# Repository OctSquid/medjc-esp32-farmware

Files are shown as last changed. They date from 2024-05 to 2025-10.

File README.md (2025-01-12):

# MEDJC09-HUB

## 概要

乾式筋電センサ`MEDJC-09`を最大 3 台まで制御できるハブデバイス</br>
センサの電圧読み取りは`MCP3208`を使用する．

## ハードウェア構成

[回路図](./docs/pcb.md)

- マイコン : ESP32
- ADC : `MCP3208`
- 筋電センサ : `MEDJC-09` 最大 3 台

### ADC チャネル対応

| チャネル番号 |     説明      |
| :----------: | :-----------: |
|     `0`      | MED`0`のME値  |
|     `1`      | MED`0`のSME値 |
|     `2`      | MED`1`のME値  |
|     `3`      | MED`1`のSME値 |
|     `4`      | MED`2`のME値  |
|     `5`      | MED`2`のSME値 |
|     `6`      |  ベース電圧   |

## コマンドフォーマット

ホストから UART で特定のコマンドを定められたバイナリフォーマットで送信する．</br>
バイナリの送信受信には[PacketSerial](https://github.com/bakercp/PacketSerial/tree/master)が使用される．</br>
送受信されるパケットは`COBS`エンコードされる．以下のフォーマットはデコード後のバイナリフォーマットである．

### 送信コマンド(HOST -> ESP32)

```bash
<コマンド> <ID> <パラメータ(オプション)>
[CMD] [ID] [PRM]
```

- `コマンド` : コマンド一覧のコマンドを送信する．コマンド一覧を参照．
- `ID` : コマンド送受信を対応させるための識別子. 16bit符号なし整数.
- `パラメータ` : コマンドによって送信するパラメータのサイズは異なる．

### 応答コマンド(ESP32 -> HOST)

コマンドが正常に処理された場合，ACK 応答を経た後，応答コマンドを返す．</br>

```bash
<応答コマンド> <ID> <パラメータ(オプション)>
[CMD] [ID] [PRM]
```

- `応答コマンド` : コマンド一覧の応答コマンドを返す．
- `ID` : コマンド送受信を対応させるための識別子. 16bit符号なし整数.
- `パラメータ` : コマンドによって返すパラメータのサイズは異なる．

> [!NOTE]
> すべてのコマンドはCOBSエンコードされて送受信されます。

### ERR 応答(ESP32 -> HOST)

コマンドが正常に処理されなかった場合，エラーコマンドを返す．</br>
特定のコマンドに対応するエラーコードがある．

```bash
# 0xFE <ERRコード> 0xFD
[SER] [ERRCode] [EER]
```

- `SERTX` : エラー応答の開始を示す．エラー応答の開始には必ず SERTX`0xFE`を返す．
- `ERRコード` : エラーコードを返す．ERR コード一覧を参照．
- `EERTX` : エラー応答の終了を示す．エラー応答の終了には必ず EERTX`0xFD`を返す．

#### ERR コード一覧(共通)

| ERR コード |               エラー内容               |
| :--------: | :------------------------------------: |
|   `0x01`   |            コマンド構文不正            |
|   `0x11`   |   コマンド無効(対応するコマンドなし)   |
|   `0x21`   | パラメータ無効(対応するパラメータなし) |

### コマンド一覧

- ファームウェアバージョンの取得
- ベース電圧の取得
- センサの接続状態の確認
- センサの ME 読み取り
- センサの SME 読み取り

| コマンド | コマンド名 |          コマンド説明          |
| :------: | :--------: | :----------------------------: |
|  `0x00`  |   `PING`   |       デバイスの生存確認       |
|  `0x01`  |  `GETVER`  | ファームウェアバージョンの取得 |
|  `0x02`  |  `GETBV`   |        ベース電圧の取得        |
|  `0x20`  |  `GETCON`  |     センサの接続状態の確認     |
|  `0x30`  |  `GETME`   |      センサの ME 読み取り      |
|  `0x31`  |  `GETSME`  |     センサの SME 読み取り      |
|  `0x40`  |  `STAPRM`  | ポーリングレポートモードの開始 |
|  `0x41`  |  `ENDPRM`  | ポーリングレポートモードの終了 |
|  `0x42`  |  `SETPRR`  | ポーリングレポートレートの設定 |
|  `0x43`  |  `GETPRR`  | ポーリングレポートレートの取得 |
|  `0x4F`  |  `GETPR`   |    ポーリングレポートの取得    |

#### デバイスの生存確認

デバイスの生存確認を行う．

- 送信コマンド

```bash
0x00 [ID]
```

- 応答コマンド

```bash
0x00 [ID]
```

#### ファームウェアバージョンの取得

デバイスのファームウェアバージョンを取得する．

- 送信コマンド

```bash
0x01 [ID]
```

- 応答コマンド

```bash
0x01 [ID] [MJV] [MIV] [PTV]
# EX) 0x01 0x0000 0x01 0x00 0x00 -> v1.0.0
```

| パラメータ | サイズ  |        説明        |
| :--------: | :-----: | :----------------: |
|   `MJV`    | `1byte` | メジャーバージョン |
|   `MIV`    | `1byte` | マイナーバージョン |
|   `PTV`    | `1byte` |  パッチバージョン  |

#### ベース電圧の取得

デバイスのベース電圧を取得する．

- 送信コマンド

```bash
0x02 [ID]
```

- 応答コマンド

```bash
0x02 [ID] [VB]
# EX) 0x02 0x0000 0xFFFF -> 3.3V
```

| パラメータ | サイズ  |                                  説明                                   |
| :--------: | :-----: | :---------------------------------------------------------------------: |
|    `VB`    | `2byte` | ベース電圧.符号あり 16bit 整数.`0-3.3`V を`0-4095`の範囲に置き換えた値. |

- ベース電圧について

コマンドで得られた値を$`v_B`$とすると，ベース電圧$`V_B`$は次のように表される．

$$
\begin{align}
V_B = \frac{3.3}{4095} \times v
\end{align}
$$

#### センサの接続状態の確認

> [!CAUTION]
> v1.2.0 以降では MCP3208 を使用するため，このコマンドは機能しない．

デバイスに接続されているセンサの接続状態を確認する．

- 送信コマンド

```bash
0x20 [ID]
```

- 応答コマンド

```bash
0x20 [ID] [CON0] [CON1] [CON2] [CON3]
# EX) 0x20 0x0000 0x01 0x00 0x00 0x00 -> センサ0: 接続, センサ1: 未接続, センサ2: 未接続, センサ3: 未接続
```

|      パラメータ      | サイズ  |                             説明                              |
| :------------------: | :-----: | :-----------------------------------------------------------: |
| `CON{n}` (`n`:`0-3`) | `1byte` | センサの接続状態(`0x00`: `disconnected`, `0x01`: `connected`) |

#### センサの ME 読み取り

デバイスに接続されているセンサの ME 値を読み取る．

- 送信コマンド

```bash
0x30 [ID]
```

- 応答コマンド

```bash
0x30 [ID] [ME0] [ME1] [ME2] [ME3]
# EX) 0x30 0x0000 0x03 0xE8 0x03 0xE9 0x00 0x00 0x00 0x00 -> ME0: 1000, ME1: 1001, ME2: 0, ME3: 0
```

|     パラメータ     | サイズ  |                                      説明                                      |
| :----------------: | :-----: | :----------------------------------------------------------------------------: |
| `ME{n}`(`n`:`0-3`) | `2byte` | ME 値. 符号あり 16bit 整数の上位 bit・下位 bit.センサが接続されていない場合`0` |

- ME 値について

筋電信号 ME を $`E`$ とすると

$$
\begin{align}
- 2048 \leq E \leq  2047\\
\end{align}
$$

ベース電圧(V)を $`V_B`$ すると，筋電信号電圧 $`V_{E}`$ は次のように表される．

$$
\begin{align}

V_{E} = \begin{cases}
            \frac{E}{2047} \times V_B & (E \geq 0) \\
            \frac{E}{2048} \times V_B & (E < 0) \\
        \end{cases}
\\

- \frac{1}{2} V_B \leq V_{E} \leq \frac{1}{2} V_B \\

\end{align}
$$

#### センサの SME 読み取り

デバイスに接続されているセンサの SME 値を読み取る．

- 送信コマンド

```bash
0x31 [ID]
```

- 応答コマンド

```bash
0x31 [ID] [SME0] [SME1] [SME2] [SME3]
# EX) 0x31 0x0000 0x07 0xD0 0x07 0xD1 0x00 0x00 0x00 0x00 -> SME0: 2000, SME1: 2001, SME2: 0, SME3: 0
```

|     パラメータ      | サイズ  |                                      説明                                      |
| :-----------------: | :-----: | :----------------------------------------------------------------------------: |
| `SME{n}`(`n`:`0-3`) | `2byte` | SME 値.符号あり 16bit 整数の上位 bit・下位 bit.センサが接続されていない場合`0` |

- SME 値について

整流・平滑筋電信号 SME を $`E'`$ とすると

$$
\begin{align}
0 \leq E' \leq 4095 \\
\end{align}
$$

ベース電圧(V)を $`V_B`$ すると，整流・平滑筋電信号電圧 $`V_{E'}$ は次のように表される．

$$
\begin{align}
V_{E'} = \frac{E'}{4095} \times V_B \\
0 \leq V_{E'} \leq V_B \\
\end{align}
$$

#### ポーリングレポートモードの開始

デバイスの情報一定間隔で自動的に送信するモードの開始．
[ポーリングレポートの取得](#ポーリングレポートの取得)で得られる応答コマンドを設定されたレートで送信する．
なお，ポーリングレポートモードで送信されたレポートのIDは`0`となる．

- 送信コマンド

```bash
0x40 [ID]
```

- 応答コマンド

```bash
0x40 [ID]
```

#### ポーリングレポートモードの終了

デバイスのポーリングレポートモードを終了する．

- 送信コマンド

```bash
0x41 [ID]
```

- 応答コマンド

```bash
0x41 [ID]
```

#### ポーリングレポートレートの設定

デバイスのポーリングレポートレートをHzで設定する．

- 送信コマンド

```bash
0x42 [ID] [RATE]
# EX) 0x42 0x0000 0x00 0x64 -> 100hz
```

| パラメータ | サイズ  |                                       説明                                       |
| :--------: | :-----: | :------------------------------------------------------------------------------: |
|   `RATE`   | `2byte` | ポーリングレポートレート.符号あり 16bit 整数の上位 bit・下位 bit. Hzで設定する． |

- 応答コマンド

```bash
0x42 [ID]
```

#### ポーリングレポートレートの取得

デバイスのポーリングレポートレートを取得する．

- 送信コマンド

```bash
0x43 [ID]
```

- 応答コマンド

```bash
0x43 [ID] [RATE]
# EX) 0x43 0x0000 0x00 0x64 -> 100Hz
```

| パラメータ | サイズ  |                                 説明                                  |
| :--------: | :-----: | :-------------------------------------------------------------------: |
|   `RATE`   | `2byte` | ポーリングレポートレート(Hz).符号あり 16bit 整数の上位 bit・下位 bit. |

#### ポーリングレポートの取得

デバイスのポーリングレポートを取得する．

- 送信コマンド

```bash
0x4F [ID]
```

- 応答コマンド

```bash
0x40 [ID] [VB] [ME0] [ME1] [ME2] [ME3] [SME0] [SME1] [SME2] [SME3] [TMP]
```

|     パラメータ      | サイズ  |                                                   説明                                                    |
| :-----------------: | :-----: | :-------------------------------------------------------------------------------------------------------: |
|        `VB`         | `2byte` |                   ベース電圧.符号あり 16bit 整数.`0-5`V を`0-4095`の範囲に置き換えた値.                   |
| `ME{n}`(`n`:`0-3`)  | `2byte` |              ME 値. 符号あり 16bit 整数の上位 bit・下位 bit.センサが接続されていない場合`0`               |
| `SME{n}`(`n`:`0-3`) | `2byte` |              SME 値.符号あり 16bit 整数の上位 bit・下位 bit.センサが接続されていない場合`0`               |
|        `TMP`        | `4byte` | レポート送信時のタイムスタンプ. ESP32 が起動してからの時間(ms). 符号なし 32bit 整数を 4 分割した byte 列. |

各パラメータの詳細は該当するコマンドの説明を参照．

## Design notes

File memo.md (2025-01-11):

# メモ

最新版のPIOだとなぜかVSCodeのTest Explorer UIでテストの出力が表示されない場合があるので，その時は以下のコマンドでテストを実行する．

```sh
pio test -vv
```

また，テストを実行する時は，C3-superminiだと面倒なので，esp32devを使う．
C3のほうは書き込みモードにするために，毎回ボードのBOOTボタンを押しながらリセットボタンを押す必要があり面倒．

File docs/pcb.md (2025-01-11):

# 基板仕様

## 回路図



## 部品表

| #    | Reference                     | Value              | Qty  | Desc             | URL                                                        |
| :--- | :---------------------------- | :----------------- | :--- | :--------------- | :--------------------------------------------------------- |
| 1    | RV1                           | 5kΩ                | 1    | 半固定抵抗       | [GF063P](https://akizukidenshi.com/catalog/g/g114904/)     |
| 2    | R6,R9,R10                     | 200Ω               | 3    | カーボン抵抗     | [1/4W200](https://akizukidenshi.com/catalog/g/g125201/)    |
| 3    | R3,R4,R5,R7,R8,R11,R12        | 10kΩ               | 7    | カーボン抵抗     | [1/4W10k](https://akizukidenshi.com/catalog/g/g125103/)    |
| 4    | R1,R2,R13                     | 33kΩ               | 3    | カーボン抵抗     | [1/4W33k](https://akizukidenshi.com/catalog/g/g125333/)    |
| 6    | J5                            | Conn_01x02_Pin     | 1    | ピンヘッダ       | [PH-1x40SG](https://akizukidenshi.com/catalog/g/g100167/)  |
| 7    | J2,J3,J4                      | Conn_01x05_Socket  | 3    | ピンソケット     | [FHU-1x42SG](https://akizukidenshi.com/catalog/g/g105779/) |
| 8    | J1                            | MJ-179PH           | 1    | DCジャック       | [MJ-179PH](https://akizukidenshi.com/catalog/g/g106568/)   |
| 9    | D1                            | 1N4007             | 1    | ダイオード       | [1N4007](https://akizukidenshi.com/catalog/g/g100934/)     |
| 10   | C10,C11,C15                   | 1μF                | 3    | コンデンサ       | [1uF50v](https://akizukidenshi.com/catalog/g/g104066/)     |
| 11   | C8,C9,C16                     | 0.47μF             | 3    | コンデンサ       | [0.47uF50v](https://akizukidenshi.com/catalog/g/g115938/)  |
| 12   | C4                            | 47μF               | 1    | 電源用コンデンサ | [47uF63v](https://akizukidenshi.com/catalog/g/g117403/)    |
| 13   | C1,C2,C3,C5,C6,C7,C12,C13,C14 | 0.1μF              | 9    | コンデンサ       | [0.1uF50v](https://akizukidenshi.com/catalog/g/g100090/)   |
| 14   | U2                            | BA033CC0T          | 1    | レギュレータ     | [BA033CC0T](https://akizukidenshi.com/catalog/g/g113675/)  |
| 15   | U7                            | MCP3208-CI_P       | 1    | ADC              | [MCP3208](https://akizukidenshi.com/catalog/g/g100238/)    |
| 16   | U6                            | NJM2747D           | 1    | オペアンプ       | [NJM2747D](https://akizukidenshi.com/catalog/g/g109117/)   |
| 17   | U3,U4,U5                      | MERB-09            | 3    | 筋電センサ       |                                                            |
| 18   | U1                            | ESP32-C3_SUPERMINI | 1    | マイコン         |                                                            |

- オプション

| #    | Reference | Value          | Qty  | Desc                 | URL                                                        |
| :--- | :-------- | :------------- | :--- | :------------------- | :--------------------------------------------------------- |
| 1    | J6        | Conn_01x02_Pin | 1    | ジャンパピン         | [MJ-254-6BK](https://akizukidenshi.com/catalog/g/g103687/) |
| 2    | U6        | Conn_01x02_Pin | 1    | ICソケット           | [2227-16](https://akizukidenshi.com/catalog/g/g100007/)    |
| 3    | -         | M3x6           | 4    | 基板取り付けネジ     | [M3x6](https://akizukidenshi.com/catalog/g/g110245/)       |
| 4    | -         | M3x0.5         | 4    | 基板取り付けナット   | [M3x0.5](https://akizukidenshi.com/catalog/g/g111521/)     |
| 5    | -         | M3-10-4        | 4    | 基板取り付けスペーサ | [M3-10-4](https://akizukidenshi.com/catalog/g/g108164/)    |
| 6    | -         | -              | 4    | ゴム足               | [020-001](https://akizukidenshi.com/catalog/g/g116317/)    |

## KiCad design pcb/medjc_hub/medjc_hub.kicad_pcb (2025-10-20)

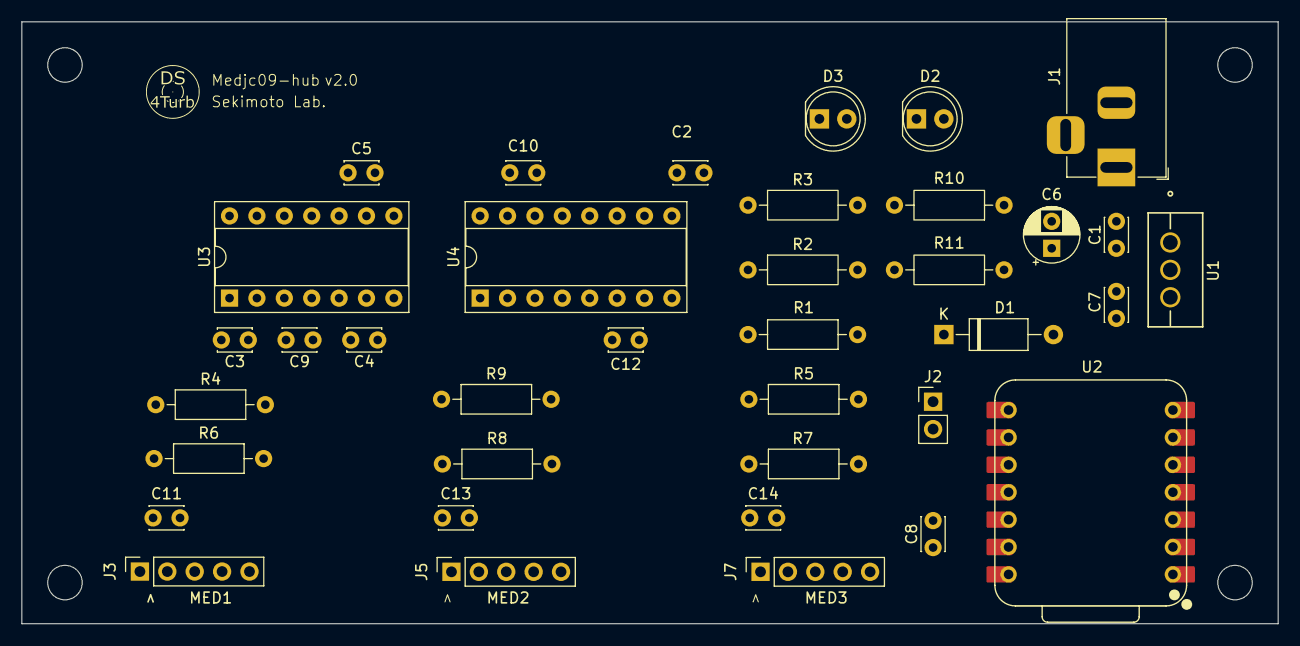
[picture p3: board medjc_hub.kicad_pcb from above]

Board: 2 copper layers, 116.5 x 55.8 mm, 41 parts (0 on the bottom side), 27 nets, no tracks yet.

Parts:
C1, C2, C3, C4, C5, C7, C8, C9, C10, C11, C12, C13, C14: 0.1μF; C_Disc_D3.0mm_W2.0mm_P2.50mm
C6: 47μF; CP_Radial_D5.0mm_P2.50mm
D1: 1N4007; D_A-405_P10.16mm_Horizontal
D2, D3: LED; LED_D5.0mm
J1: MJ-180P; BarrelJack_Horizontal
J2: Conn_01x02_Pin; PinHeader_1x02_P2.54mm_Vertical
J3, J5, J7: Conn_01x05_Socket; PinSocket_1x05_P2.54mm_Vertical
R1, R2, R4, R5, R6, R7, R8, R9: 10kΩ; R_Axial_DIN0207_L6.3mm_D2.5mm_P10.16mm_Horizontal
R3: 5kΩ; R_Axial_DIN0207_L6.3mm_D2.5mm_P10.16mm_Horizontal
R10, R11: 200Ω; R_Axial_DIN0207_L6.3mm_D2.5mm_P10.16mm_Horizontal
REF1, REF2, REF3, REF4: MountingHole_3.2mm_M3
U1: BA033CC0T
U2: XIAO-ESP32-S3-DIP; XIAO-ESP32S3-DIP
U3: NJM2747D; DIP-14_W7.62mm_Socket
U4: MCP3208-CI_P; DIP-16_W7.62mm_Socket

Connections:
+3V3: C9.1, C10.1, C11.1, C12.1, C13.1, C14.1, D1.1 (K), J2.2, J3.1, J5.1, J7.1, R1.1, U3.4 (+Vin), U4.7 (CH6), U4.15 (VREF), U4.16 (VDD)
FME1: R4.2, U3.1 (OUT_A), U4.1 (CH0)
FME2: R9.2, U3.7 (OUT_B), U4.3 (CH2)
FME3: R5.1, U3.8 (OUT_C), U4.5 (CH4)
GND: C1.2, C2.2, C3.2, C4.2, C5.2, C6.2, C7.1, C8.2, C9.2, C10.2, C11.2, C12.2, C13.2, C14.2, D2.1 (K), D3.1 (K), J1.2, J3.3, J5.3, J7.3, R2.2, R3.2, U1.2 (N.C./GND), U2.13 (GND), U3.11 (GND), U4.9 (DGND), U4.14 (AGND)
IN_AMP_A: C2.1, C3.1, C4.1, C5.1, R1.2, R2.1, R3.1, U3.3 (+IN_A), U3.5 (+IN_B), U3.10 (+IN_C)
MISO: U2.10 (D9), U4.12 (DOUT)
MOSI: U2.11 (D10), U4.11 (DIN)
unnamed: C6.1, C7.2, D1.2 (A), U1.3 (OUT)
unnamed: D2.2 (A), R10.2
unnamed: D3.2 (A), R11.2
unnamed: C8.1, J2.1, U2.12 (VCC_3V3)
unnamed: J3.4, J5.4, J7.4
unnamed: C1.1, J1.1, U1.1 (Vcc)
unnamed: R4.1, R6.2, U3.2 (-IN_A)
unnamed: R8.2, R9.1, U3.6 (-IN_B)
unnamed: R5.2, R7.1, U3.9 (-IN_C)
POWER_LED: R10.1, U2.4 (D3)
RAWME1: J3.2, R6.1
RAWME2: J5.2, R8.1
RAWME3: J7.2, R7.2
SCK: U2.9 (D8), U4.13 (CLK)
SME1: J3.5, U4.2 (CH1)
SME2: J5.5, U4.4 (CH3)
SME3: J7.5, U4.6 (CH5)
SS: U2.6 (D5), U4.10 (~CS/SHDN)
STATUS_LED: R11.1, U2.5 (D4)

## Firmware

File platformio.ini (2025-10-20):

; PlatformIO Project Configuration File
;
;   Build options: build flags, source filter
;   Upload options: custom upload port, speed and extra flags
;   Library options: dependencies, extra library storages
;   Advanced options: extra scripting
;
; Please visit documentation for the other options and examples
; https://docs.platformio.org/page/projectconf.html

[platformio]
default_envs = esp32dev
extra_configs = ports.ini

[env:esp32dev]
platform = espressif32
board = esp32dev
framework = arduino
monitor_speed = 921600
test_speed = 921600
build_unflags = -Os
build_flags = -O3
lib_deps =
	SPI
	bakercp/PacketSerial@^1.4.0
	robtillaart/MCP_ADC@^0.5.1

[env:esp32-c3-devkitm-1]
platform = espressif32
board = esp32-c3-devkitm-1
framework = arduino
monitor_speed = 921600
test_speed = 921600
build_unflags = -Os
build_flags =
	-O3
	-D ARDUINO_USB_CDC_ON_BOOT=1
	-D ARDUINO_USB_MODE=1
lib_deps =
	SPI
	bakercp/PacketSerial@^1.4.0
	robtillaart/MCP_ADC@^0.5.1

[env:seeeduino_xiao]
platform = https://github.com/Seeed-Studio/platform-seeedboards.git
board = seeed-xiao-c3
framework = arduino
monitor_speed = 921600
test_speed = 921600
build_unflags = -Os
build_flags =
	-O3
	-D ARDUINO_USB_CDC_ON_BOOT=1
	-D ARDUINO_USB_MODE=1
lib_deps =
	SPI
	bakercp/PacketSerial@^1.4.0
	robtillaart/MCP_ADC@^0.5.1

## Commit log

2024-05-26 🎉 Init: プロジェクト作成
2024-05-26 ✨ Add: 基本機能実装
2024-05-26 ✅ Add: テスト追加
2024-05-26 👷 Add: GithubActions Build 追加
2024-05-26 💚 Fix: extra_configsのセクションを修正
2024-05-26 🙈 Add: ports.ini
2024-05-26 🔥 Remove: ports.ini
2024-05-26 📝 Update: 応答コマンドバイナリの仕様変更に対応
2024-05-26 🔥 Remove: ACK応答を削除
2024-05-26 📝 Add: ポーリングレポートモードの仕様を追加
2024-05-26 ✨ Add: ポーリングレポートモードのコマンド追加
2024-05-26 ✅ ポーリングレポートモードのテスト追加
2024-05-26 🔧 Remove: 不要な設定の削除
2024-05-26 🔥 Remove: デバッグ用のコードの削除
2024-05-27 📝 Update: ポーリングレポートコマンドの仕様を変更
2024-05-27 ✨ Add: ポーリングレポート取得コマンドを追加
2024-05-27 ✅ Add: ポーリングレポート取得コマンドのテストを追加
2024-05-27 ⚡️ Improve: ads1115の読み取り速度の高速化
2024-05-27 ⚡️ Improve: 高速化
2024-05-27 ⚡️ Update: レポートの余分なデータを削除
2024-05-27 ✨ Add: レポートにタイムスタンプを追加
2024-05-27 ✅ Add: タイムスタンプのテストを追加
2024-05-27 ⚡️ Improve: マルチタスク化
2024-05-27 ⚡️ Improve: hwタイマーを使用するように変更
2024-05-27 ✅ Update: テストでupdate()を使用しないよう更新
2024-05-27 🐛 Fix: SMEの読み取りチャネルを修正
2024-05-29 ⚡️ Improve: I2Cのクロックスピードを向上
2024-05-29 📝 Update: レートの指定をHzで行うように変更
2024-05-29 💥 Update: ポーリングレートをHzで指定するように
2024-05-29 ✅ Test: ポーリングレートの仕様変更に対応
2024-05-29 ⚡️ Improve: マイクロ秒単位で実行できるように
2024-05-29 🔧 Add: ビルドオプションを追加
2024-05-29 ⚡️ Improve: sendReportにIRAM_ATTR修飾子を追加
2024-05-29 💥 Change: ADCをstatic化
2024-05-29 🚑 Fix: virtual つけ忘れ
2024-05-29 🤡 Mock: ADCのモック
2024-05-29 ✅ Test: ADCのstatic化に対応
2024-05-29 💥 Change: コマンドハンドラのstatic化
2024-05-29 🤡 Mock: コマンドハンドラ用Mock
2024-05-29 ✅ Test: コマンドハンドラのテストに対応
2024-05-29 ⚡️ Improve: packetの監視処理をcore1で実行
2024-05-30 🎨 Style: inline 修飾子の位置を調整
2024-05-30 ⚡️ Improve: ボーレートを 921600 bps に設定
2024-05-30 ⚡️ Improve: ポーリングの送信処理をupdate関数で行うように変更
2024-05-30 ✅ Test: テストのボートレートを 921600bps に設定
2024-05-30 📝 Doc: コメントを追加
2024-05-30 🎨 Change: バージョン番号をマクロに変更
2024-05-30 ✨ Update: バージョンインクリメント 1.1.0
2024-05-30 🔥 Remove: 不要なinclude削除
2024-05-30 🎨 Style: format
2024-05-31 🙈 Add: .DS_Store
2024-05-31 🚧 WIP: kicad回路図を追加
    [medjc_hub.kicad_pcb, medjc_hub.kicad_sch]
2024-06-03 🚧 WIP: Kicad 回路図を更新
    [medjc_hub.kicad_sch]
2024-07-06 📝 Update: 回路図を更新
    [medjc_hub.kicad_pcb, medjc_hub.kicad_sch, simulate.kicad_pcb, simulate.kicad_sch]
2024-07-14 💥 Update: MCP3208に適用
2024-07-14 🔧 Add: c3 super mini用の構成を追加
2024-07-14 ✨ Update: バージョンインクリメント 1.2.0
2024-07-14 📝 Update: ハード仕様を更新
2024-07-14 🐛 Fix: ME値とSME値の計算が逆になっていたのを修正
2024-07-14 📝 Update: MCP3208に適用
2024-07-16 ✨ add: pingコマンドを実装
2024-07-16 🐛 fix: pingコマンドのハンドラの追加し忘れ
2024-07-23 ➖ remove: 不要な依存関係の削除
2024-07-23 ✨ feat: ADCにreadAll系関数を追加
2024-07-23 ✨ feat: コマンドの送受信にIDが必要に
2024-07-23 🔥 remove: 不要なinclude文を削除
2024-07-23 📝 update: コマンド構文を更新(ID)
2024-07-23 ✅ test: テストを新コマンド構文に対応
2024-07-23 ✨ update: バージョン変更 1.4.0
2025-01-11 📝 Update: 部品情報を更新
2025-01-11 📝 Update: アクティブレイヤーを0に変更
2025-01-11 ✨ update: ボード設定をesp32-c3-devkitm-1に変更
2025-01-11 📝 add: テスト実行に関するメモを追加
2025-01-11 ✨ update: コマンドパーサーのバッファ処理を簡素化し、STX/ETXを削除
2025-01-11 🩹 fix: パラメータの開始位置の修正
2025-01-11 🔖 update: バージョン番号を1.4から1.5に更新
2025-01-12 📝 docs: READMEにポーリングレポートモードのIDについての説明を追加
2025-10-05 ✨ add: seeeduino_xiao環境をplatformio.iniに追加
2025-10-05 Update simulation waveform colors and add NJM2747D symbol library
    - Changed the waveform color for the input voltage (VIN) to a new RGB value.
    - Updated the waveform color for the output voltage (VOUT) to a different RGB value.
    - Added cursor formatting for both VIN and VOUT signals in the simulation.
    - Introduced a new symbol library for the NJM2747D component in the project.
    [medjc_hub.kicad_pcb, medjc_hub.kicad_sch, simulate.kicad_sch]
2025-10-20 🍱 update: pcb v2
    [medjc_hub.kicad_pcb, medjc_hub.kicad_sch, simulate.kicad_sch]
2025-10-20 🚑 fix: 末尾に空白を含んだパスを修正
